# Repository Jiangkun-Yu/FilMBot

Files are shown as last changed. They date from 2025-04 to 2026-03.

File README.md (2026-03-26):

# 📦 FilMBot – A Film-based Electromagnetic Micromanipulator
FilMBot (Film-based ElectroMagnetic driven Robot) is an open-source, low-cost, and DIY-friendly micromanipulator. Designed for high-resolution micromanipulation tasks, FilMBot combines electromagnetic actuation with a soft, film-based kinametic structure to achieve sub-10 μm precision and fast response, all at a total cost of around €100.

This repository provides all necessary hardware files, firmware, and fabrication guidance to replicate and customize FilMBot for use in research, education, or hobby projects.

📄 You can find the original research paper describing FilMBot here: https://doi.org/10.48550/arXiv.2410.23059

## 📁 Project Structure

FilMBot/<br>
│<br>
├── hardware/               &emsp;&emsp;&emsp;&emsp;&emsp;&emsp;&emsp;&emsp;&emsp;&emsp;&emsp;&emsp;&emsp;&emsp;&emsp;&emsp;# Electronics & mechanical design<br>
│   &emsp;&emsp;├── 3D models/           &ensp;&emsp;&emsp;&emsp;&emsp;&emsp;&emsp;&emsp;&emsp;&emsp;&emsp;&emsp;&emsp;# STL files for 3D printed parts<br>
│   &emsp;&emsp;├── cut patterns/        &emsp;&emsp;&emsp;&emsp;&emsp;&emsp;&emsp;&emsp;&emsp;&emsp;&emsp;&emsp;# Laser-cut/printable patterns for film structure<br>
│   &emsp;&emsp;└── schematic and PCB    &ensp;&emsp;&emsp;&emsp;&emsp;&emsp;&emsp;&emsp;&emsp;&emsp;# PCB schematics, board layout, Gerber files ... <br>
│   		&emsp;&emsp;&emsp;&emsp;&emsp;├── 01 Gerber file for ordering PCB/<br>
│   		&emsp;&emsp;&emsp;&emsp;&emsp;├── 02 schematic and bill of electronic components.pdf/<br>
│   		&emsp;&emsp;&emsp;&emsp;&emsp;├── 03 Mega 2560 Rev3_datasheet_from docs.arduino.cc.pdf/<br>
│   		&emsp;&emsp;&emsp;&emsp;&emsp;├── 04 TB6612FNG Hookup Guide.txt/	<br>
│   		&emsp;&emsp;&emsp;&emsp;&emsp;└── 05 TB6612FNG datasheet.pdf/<br>
│<br>
├── firmware/                &emsp;&emsp;&emsp;&emsp;&emsp;&emsp;&emsp;&emsp;&emsp;&emsp;&emsp;&emsp;&emsp;&emsp;&emsp;&emsp;# Arduino firmware<br>
│   &emsp;&emsp;└── FilMBot_Arduino_Code/ <br>
│<br>
├── materials, components and fabrication/     &emsp;&emsp;&emsp;# Cost analysis & fabrication details<br>
│   &emsp;&emsp;└── materials, components and fabrication.docx/<br>
│<br>
└── README.md                &emsp;&emsp;&emsp;&emsp;&emsp;&emsp;&emsp;&emsp;&emsp;&emsp;&emsp;&emsp;&emsp;&emsp;&emsp;# Project overview (this file)<br>

## 🛠️ Hardware Overview
The hardware system includes:

&emsp;&emsp;&emsp;&emsp;&emsp;Microcontroller: Arduino Mega 2560 or compatible ATmega2560 board

&emsp;&emsp;&emsp;&emsp;&emsp;Coil driver: TB6612FNG dual-channel motor drivers

&emsp;&emsp;&emsp;&emsp;&emsp;Power: 12V DC input with step-down converters (to 5V, 3.3V, etc.)

&emsp;&emsp;&emsp;&emsp;&emsp;Interfaces: Joystick + buttons, optional LCD and sensors (current, temperature)

&emsp;&emsp;&emsp;&emsp;&emsp;Structure: Soft film-based body (laser-cut or hand-cut) with permanent magnets

&emsp;&emsp;&emsp;&emsp;&emsp;PCB: Custom-designed for compact and stable operation (or breadboard prototype)

You’ll find:

&emsp;&emsp;&emsp;&emsp;&emsp;📐 3D models in hardware/3D models/

&emsp;&emsp;&emsp;&emsp;&emsp;✂️ Cutting patterns in hardware/cut patterns/

&emsp;&emsp;&emsp;&emsp;&emsp;🔌 Circuit diagrams, PCB, and related instructions and datasheets in hardware/schematic and PCB/

## 💻 Firmware
The firmware supports two control modes:

&emsp;&emsp;&emsp;&emsp;&emsp;Joystick-based telemanipulation (standalone)

&emsp;&emsp;&emsp;&emsp;&emsp;PC command-based control via UART

It runs on a max. 1 kHz (100 Hz by default) interrupt loop for:

&emsp;&emsp;&emsp;&emsp;&emsp;Reading joystick, buttons, and sensors (current, temperature)

&emsp;&emsp;&emsp;&emsp;&emsp;Performing PID control for coil current

&emsp;&emsp;&emsp;&emsp;&emsp;Generating PWM outputs

&emsp;&emsp;&emsp;&emsp;&emsp;Sending data and debug info to LCD or PC

The firmware is modular and easy to extend. To modify or maintain:

&emsp;&emsp;&emsp;&emsp;&emsp;Change pin mappings or parameters in pin_init.h

&emsp;&emsp;&emsp;&emsp;&emsp;Add new features or control logic in FilMBot_Arduino_Code.ino

## 📉 Materials, Components & Fabrication
The total cost of FilMBot is approximately €100. All parts are selected for affordability and global availability.

In materials_and_costs/, you’ll find:

&emsp;&emsp;&emsp;&emsp;&emsp;✔️ A full Bill of Materials with prices

&emsp;&emsp;&emsp;&emsp;&emsp;🔧 A DIY fabrication guide describing each step (cutting, assembly, etc.)

&emsp;&emsp;&emsp;&emsp;&emsp;🛒 A list of suggested vendors and links

FilMBot is designed to be built with only basic tools, with no need for a CNC or cleanroom.

## 🤝 License and Citation
Please cite the original paper when using this work in academic or public projects to help spread the impact of this open-source initiative:

https://doi.org/10.1109/TRO.2026.3658292
and
https://doi.org/10.1109/MARSS65887.2025.11072791 

## 🌟 How to Contribute
We welcome contributions from the community! You can help by:

&emsp;&emsp;&emsp;&emsp;&emsp;Submitting pull requests to improve documentation, firmware, or hardware files

&emsp;&emsp;&emsp;&emsp;&emsp;Sharing your builds and variations

&emsp;&emsp;&emsp;&emsp;&emsp;Reporting issues or suggesting enhancements

Let’s work together to make micromanipulation more accessible and innovative!

## 📬 Contact
Feel free to reach out to the project author:

Jiangkun Yu

Doctoral Researcher

Robotic Instruments Group

Aalto University, Finland

📧 jiangkun.yu@aalto.fi

🌐 www.linkedin.com/in/jiangkun-yu-5265a0278

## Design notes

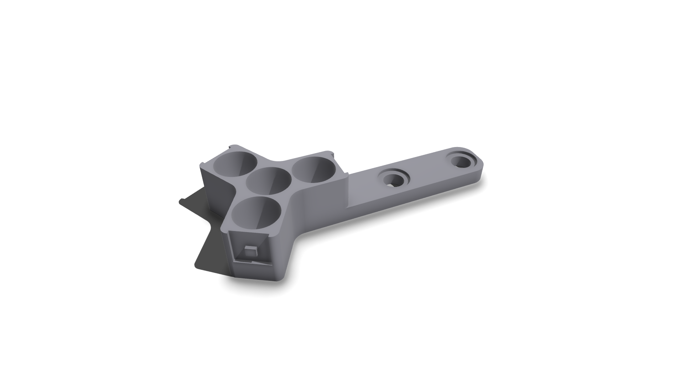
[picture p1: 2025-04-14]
hardware/3D models/Coil holder_3 legged.png

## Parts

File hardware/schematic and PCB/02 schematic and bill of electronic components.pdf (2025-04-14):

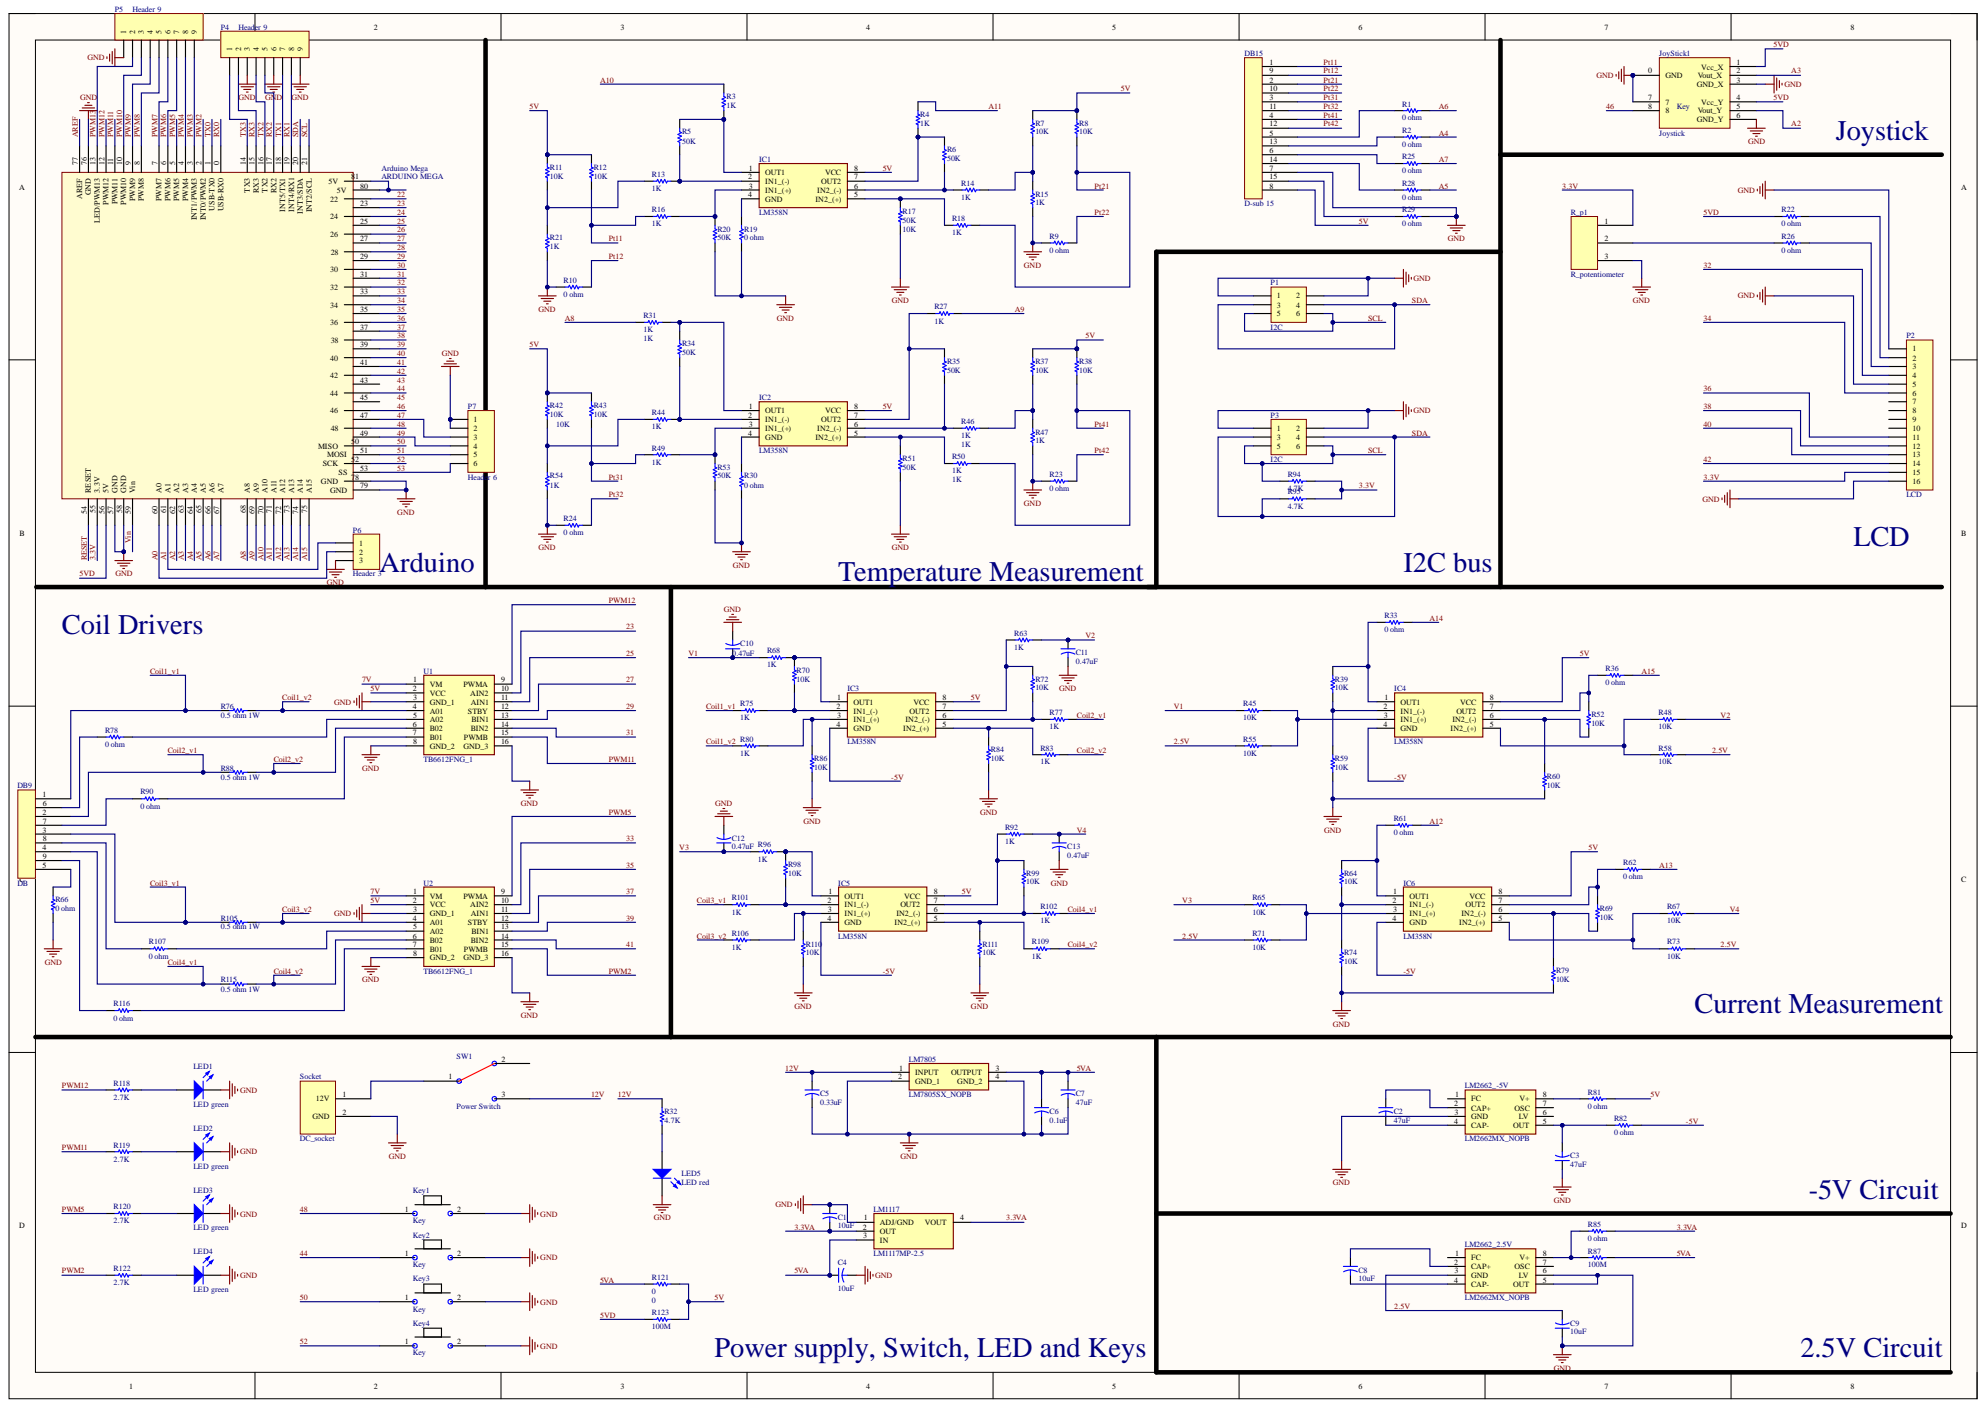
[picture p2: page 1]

6 | | 0 ohm

Coil4_v2 | B01 7 GND_2 8 | 41

47uF | CAP- 4

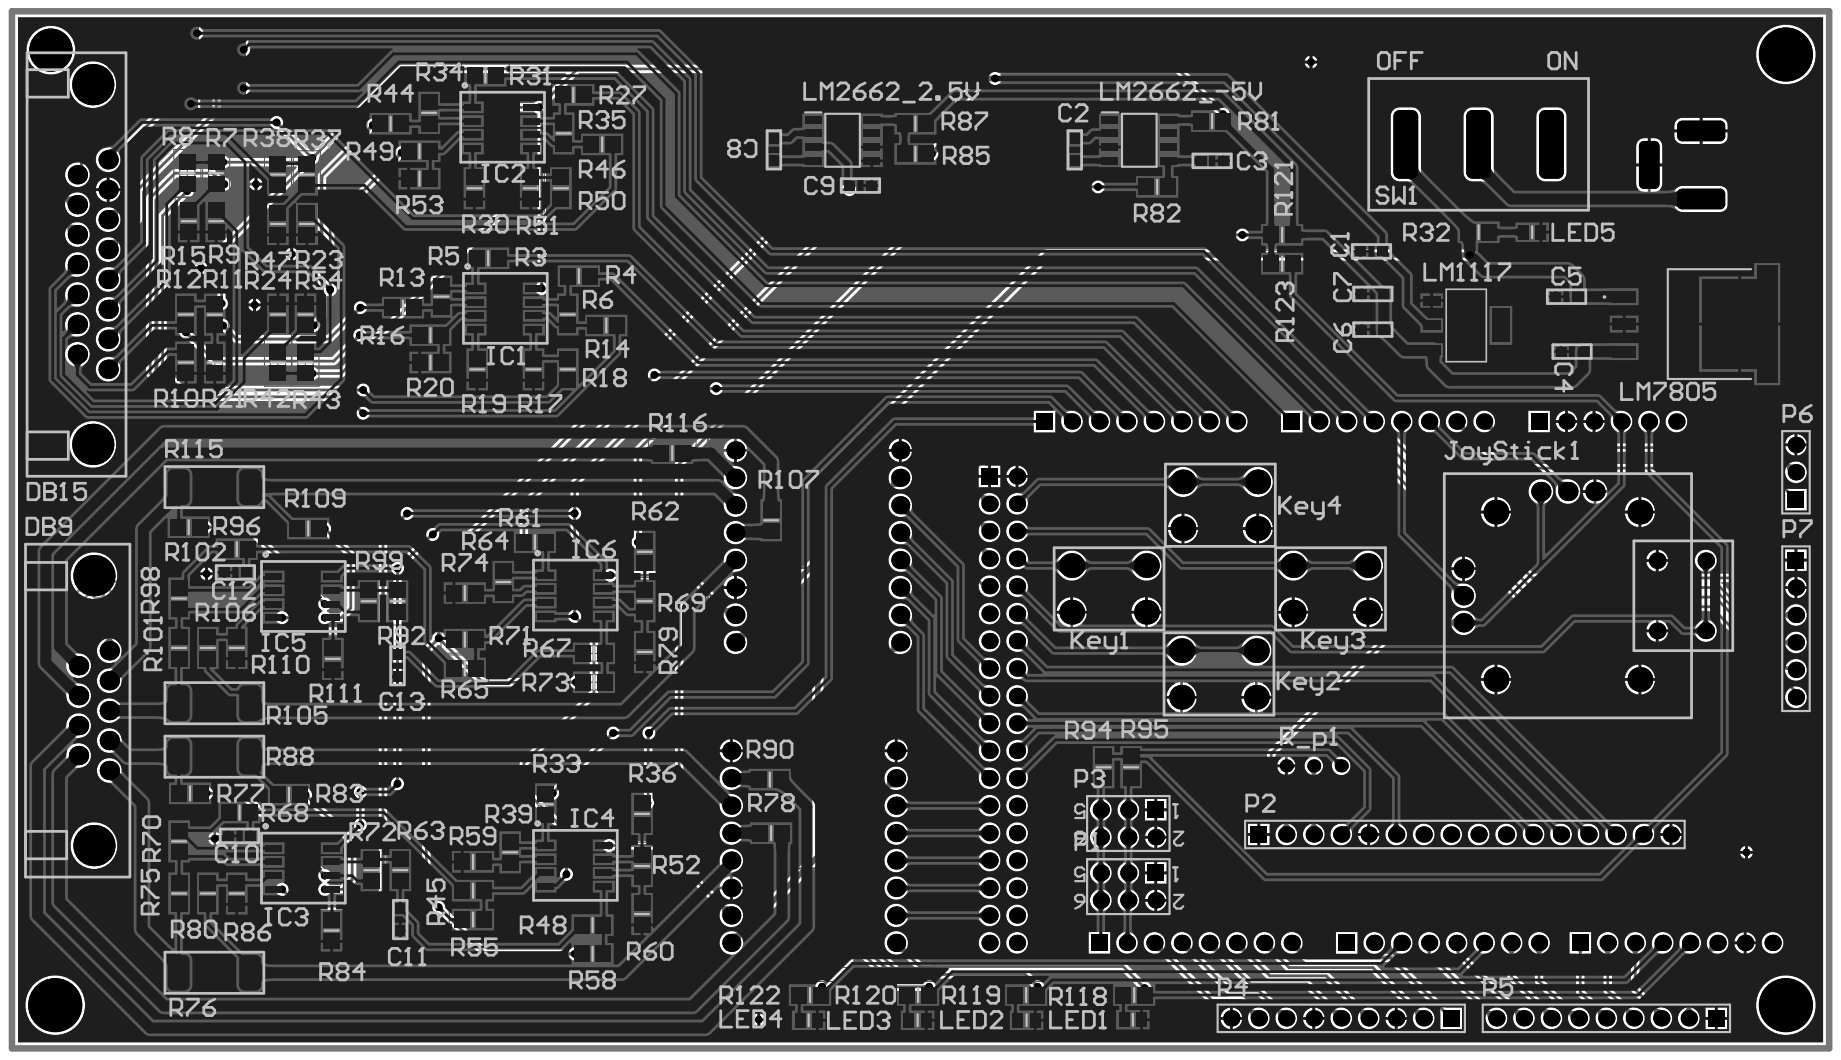
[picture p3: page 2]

Comment | Description | Designator | Footprint | LibRef | Quantity
ARDUINOMEGA | | ArduinoMega | PCBComponent_1 | ARDUINOMEGA | 1
10uF | Capacitor | C1, C4, C8, C9 | C0603 | Cap2 | 4
47uF | Capacitor | C2, C3, C7 | C0603 | Cap2 | 3
0.33uF | Capacitor | C5 | C0603 | Cap2 | 1
0.1uF | Capacitor | C6 | C0603 | Cap2 | 1
0.47uF | Capacitor | C10, C11, C12, C13 | C0603 | Cap2 | 4
DB | | DB9 | PCBComponent_1 | DB | 1
D-sub15 | | DB15 | DB15 | D-sub15 | 1
LM358N | IntegratedCircuit | IC1, IC2, IC3, IC4, IC5, IC6 | 8-SOIC | LM358N | 6
Joystick | | JoyStick1 | PCBComponent_1 | Component_1 | 1
Key | | Key1, Key2, Key3, Key4 | PCBComponent_1 | Key | 4
LEDgreen | Typical REDGaAsLED | LED1, LED2, LED3, LED4 | 6-0805_L | LED1 | 4
LEDred | Typical REDGaAsLED | LED5 | 6-0805_L | LED1 | 1
LM1117MP-2.5 | IntegratedCircuit | LM1117 | SOT230P696X180-4N | LM1117MP-2.5 | 1
LM2662MX_NOPB | IntegratedCircuit | LM2662_2.5V, LM2662_-5V | SOIC127P600X175-8N | LM2662MX_NOPB | 2
LM7805SX_NOPB | IntegratedCircuit | LM7805 | KTT0003B | LM7805SX_NOPB | 1
I2C | Header, 3-Pin, Dual row | P1, P3 | HDR2X3 | Header 3X2 | 2
LCD | Header, 16-Pin | P2 | HDR1X16 | Header 16 | 1
Header 9 | Header, 9-Pin | P4, P5 | HDR1X9 | Header 9 | 2
Header 3 | Header, 3-Pin | P6 | HDR1X3 | Header 3 | 1
Header 6 | Header, 6-Pin | P7 | HDR1X6 | Header 6 | 1
0ohm | Resistor | R1, R2, R9, R10, R19, R22, R23, R24, R25, R26, R28, R29, R30, R33, R36, R61, R62, R66, R78, R81, R82, R85, R90, R107, R116 | 6-0805_M | Res1 | 25
1K | Resistor | R3, R4, R13, R14, R15, R16, R18, R21, R27, R31, R44, R46, R47, R49, R50, R54, R63, R68, R75, R77, R80, R83, R92, R96, R101, R102, R106, R109 | 6-0805_M | Res1 | 28
50K | Resistor | R5, R6, R17, R20, R34, R35, R51, R53 | 6-0805_M | Res1 | 8
10K | Resistor | R7, R8, R11, R12, R37, R38, R39, R42, R43, R45, R48, R52, R55, R58, R59, R60, R64, R65, R67, R69, R70, R71, R72, R73, R74, R79, R84, R86, R98, R99, R110, R111 | 6-0805_M | Res1 | 32
4.7K | Resistor | R32, R94, R95 | 6-0805_M | Res1 | 3
0.5 ohm1W | Resistor | R76, R88, R105, R115 | 2512-L | Res1 | 4
100M | Resistor | R87, R123 | 6-0805_M | Res1 | 2
2.7K | Resistor | R118, R119, R120, R122 | 6-0805_M | Res1 | 4
0 | Resistor | R121 | 6-0805_M | Res1 | 1
R_potentiometer | | R_p1 | PCBComponent_1 | R_potentiometer | 1
DC_socket | | Socket | PCBComponent_1 | DC_socket | 1
Power Switch | | SW1 | PCBComponent_1 | Component_1 | 1
TB6612FNG_1 | Undefinedor Miscellaneous | U1, U2 | ROB14450 | ROB-14450 | 2

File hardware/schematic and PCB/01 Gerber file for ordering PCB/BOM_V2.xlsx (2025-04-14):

Comment | Designator | Footprint | LCSC Part #
10uF | C1, C4, C8, C9 | C0603 | C19702
47uF | C2, C3, C7 | C0603 | C140782
0.33uF | C5 | C0603 | C1615
0.1uF | C6 | C0603 | C14663
0.47uF | C10, C11, C12, C13 | C0603 | C1623
LM358N | IC1, IC2, IC3, IC4, IC5, IC6 | 8-SOIC | C504545
LED green | LED1, LED2, LED3, LED4 | 6-0805_L | C2297
LED red | LED5 | 6-0805_L | C2286
LM1117MPX-3.3 | LM1117 | SOT230P696X180-4N | C9662
LM2662MX_NOPB | LM2662_2.5V, LM2662_-5V | SOIC127P600X175-8N | C134022
LM7805SX_NOPB | LM7805 | KTT0003B | C507146
1K | R3, R4, R13, R14, R15, R16, R18, R21, R27, R31, R44, R46, R47, R49, R50, R54, R63, R68, R75, R77, R80, R83, R92, R96, R101, R102, R106, R109 | 6-0805_M | C17513
50K | R5, R6, R17, R20, R34, R35, R51, R53 | 6-0805_M | C316211
10K | R7, R8, R11, R12, R37, R38, R39, R42, R43, R45, R48, R52, R55, R58, R59, R60, R64, R65, R67, R69, R70, R71, R72, R73, R74, R79, R84, R86, R98, R99, R110, R111 | 6-0805_M | C17414
4.7K | R32, R94, R95 | 6-0805_M | C17673
0.3 ohm 1W | R76, R88, R105, R115 | 2512-L | C474208
2.7K | R118, R119, R120, R122 | 6-0805_M | C17530

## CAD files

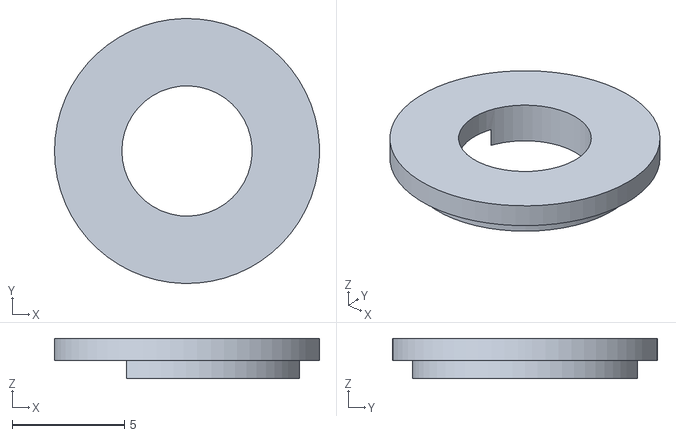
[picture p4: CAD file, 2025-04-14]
hardware/3D models/Coil shoulder_6.0mm.STL
11.8 x 11.8 x 1.80

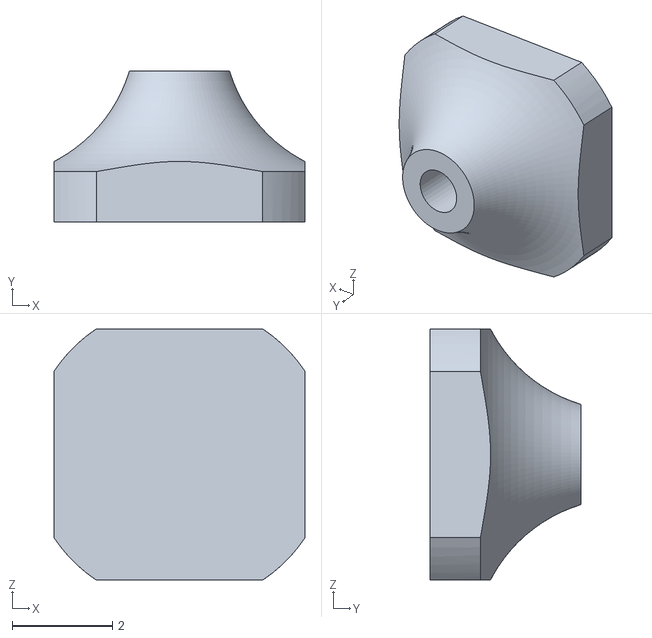
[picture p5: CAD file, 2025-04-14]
hardware/3D models/needle holder V3.STL
5.00 x 3.00 x 5.00

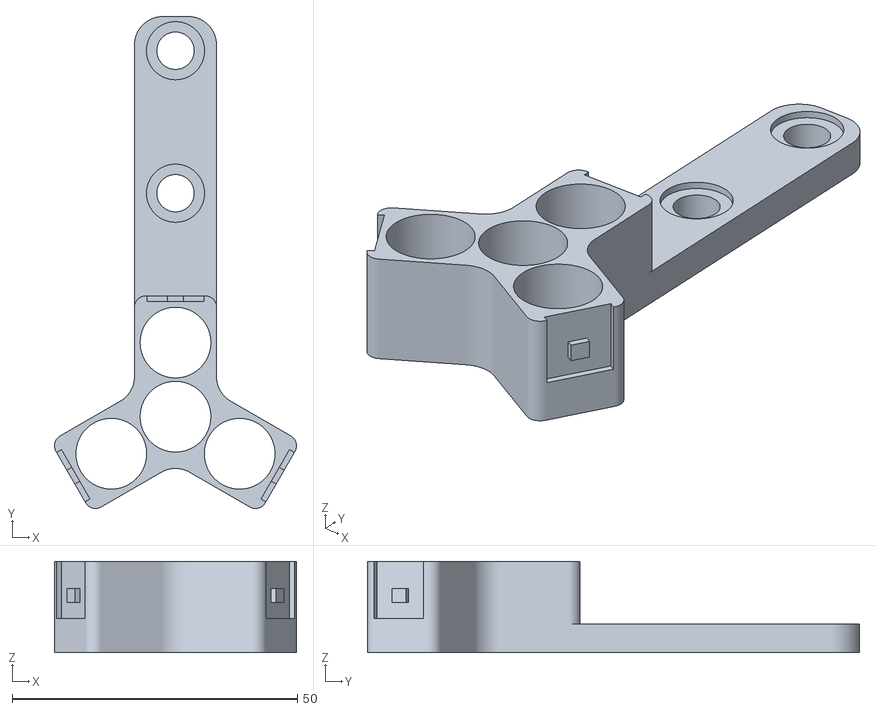
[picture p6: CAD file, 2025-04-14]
hardware/3D models/Coil holder_3 legged.stl
42.5 x 86.3 x 16.0

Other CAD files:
hardware/3D models/PCB Box_Part2_V4.STL
hardware/3D models/PCB Box_Part1_V4.STL

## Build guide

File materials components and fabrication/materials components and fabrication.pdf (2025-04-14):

FILMBOT HARDWARE COST ANALYSIS
Components | Fabrication | Price
Solenoid coils (copper wire) | Hand-wound. | 7.2 € [1]
Solenoid coil core (S355J2 steel rod) | Cutting with a saw, smoothing with a file. | 0.4 € [2]
NdFeB magnets | Direct purchasing. | 1.2 € [3]
Film (plastic or paper) | Laser-cut or print and hand-cut. | 0.2 € [4]
Needle | Heating and hot drawing, or 3D printing. | 0.2 € [5]
3D-printed components | 3D printing. | 1 € [6]
Double-side tape | Hand-cut. | 0.1 €
PCB with assembly | Direct purchasing. | 13.5 € [7]
Joystick | Soldering. | 4.2 € [8]
Microcontroller Mega 2560 | Direct purchasing. | 22.4 € [9]
Coil driver | Direct purchasing. | 20 € [10]
12V power supply | Direct purchasing. | 13.6 € [11]
Cables and connectors | Soldering. | 11 € [12]
PT1000 | Soldering. | 7.6 € [13]
Total | | 102.6 €
Please refers paper “FilMBot: A High-Speed Soft Parallel Robotic Micromanipulator” (https://doi.org/10.48550/arXiv.2410.23059) and “FilMBot: Towards 100-euro DIY-friendly high-speed robotic micromanipulator”
for detailed materials, components and fabrications.

Reference:
[1] “RS PRO 0.25mm Enamelled Copper Wire, 30 AWG 1100m Reel | RS PRO,” RS Finland. Accessed: Apr. 10, 2025.
[Online]. Available: https://fi.rsdelivers.com/product/rs-pro/rs-pro-025mm-enamelled-copper-wire-30-awg-1100m/0357716
[2] “Warma vedetty pyörötanko 6mm 1,5m.” Accessed: Apr. 10, 2025. [Online]. Available: https://www.puuilo.fi/warmavedetty-pyorotanko-6mm-1-5m
[3] W. AG, “Disc magnet self-adhesive 10 x 0,6 mm, Nickel-plated,” Supermagnete. Accessed: Apr. 10, 2025. [Online]. Available: https://www.supermagnete.fi/adhesive-magnets-neodymium/disc-magnet-self-adhesive-10mm-0.6mm_S-10-0.6-STIC
[4] “muovitasku A4/120mic 2-sivua auki värilajitelma Polypropeeni 100kpl.” Accessed: Apr. 10, 2025. [Online]. Available: https://kauppa.rckfinland.fi/130281-muovitasku-a4-120mic-2-sivua-auki-varilajitelma-polypropeeni-100kpl.html
[5] “200PCS Glass Capillary Tube Micro Hematocrit Tubing Melting Tube,” Fruugo. Accessed: Apr. 10, 2025. [Online]. Available: https://www.fruugo.fi/200pcs-glass-capillary-tube-micro-hematocrit-tubing-melting-tube-multi-purposeglass-tube-for-clinic-hospital-use-red/p-136337047-287521506?language=en
[6] “PLA 3D-filamentti Universal, 1,75 mm, 1 kg | Clas Ohlson.” Accessed: Apr. 10, 2025. [Online]. Available:
https://www.clasohlson.com/fi/PLA-3D-filamentti-Universal,-1,75-mm,-1-kg/p/38-7986-1
[7] “PCB Prototype & PCB Fabrication Manufacturer - JLCPCB.” Accessed: Apr. 10, 2025. [Online]. Available: https://jlcpcb.com/
[8] “COM-09032,” DigiKey Electronics. Accessed: Apr. 10, 2025. [Online]. Available: https://www.digikey.fi/en/products/detail/sparkfun-electronics/COM-09032/6823623
[9] “Arduino Mega 2560 R3 -yhteensopiva kehityskortti Mega2560 Ch340 | Fyndiq.” Accessed: Apr. 10, 2025. [Online].
Available: https://fyndiq.fi/tuote/arduino-mega-2560-r3-yhteensopiva-kehityskortti-mega2560-ch340-5266901d7fc74811/
[10] “2pcs TB6612FNG Dual DC Stepper Motor Driver Module, Dual Driver Controller Board H Bridge for DC Step TB6612FNG Module : Amazon.de: Business, Industry & Science.” Accessed: Apr. 10, 2025. [Online]. Available: https://www.amazon.de/TB6612FNG-Stepper-Driver-Module-Controller/dp/B09MN8F1SD/
[11] reichelt elektronik G. I. T. webmaster@reichelt.de, “V-TAC Desktop power supply, 60 W, 12 V, 5 A | Fixed-voltage
power supply units at very favourable prices | reichelt elektronik.” Accessed: Apr. 10, 2025. [Online]. Available:
https://www.reichelt.com/fi/en/shop/product/desktop_power_supply_60_w_12_v_5_a-215628
[12] “Connectors, Interconnects | D-Sub, D-Shaped Connectors | D-Sub Connector Assemblies,” DigiKey Electronics.
Accessed: Apr. 10, 2025. [Online]. Available: https://www.digikey.fi/en/products/filter/d-sub-d-shaped-connectors/d-sub-connector-assemblies/439
[13] reichelt elektronik G. I. T. webmaster@reichelt.de, “YAGEO NEXENSOS Platinum temperature sensor, Cl. B, 1000
ohms | Temperature and moisture sensors at very favourable prices | reichelt elektronik.” Accessed: Apr. 10, 2025.
[Online]. Available: https://www.reichelt.com/fi/en/shop/product/platinum_temperature_sensor_cl_b_1000_ohms-151238

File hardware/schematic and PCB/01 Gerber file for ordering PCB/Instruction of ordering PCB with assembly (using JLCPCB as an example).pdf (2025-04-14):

## Instructions for ordering PCB with assembly

Here, using JLCPCB as an example, ordering from other manufacturers will be similar.

1. Get your files ready, generally at least need all Gerber files. If you also need assembly, get BOM and CPL file ready.
2. Go to jlcpcb.com:

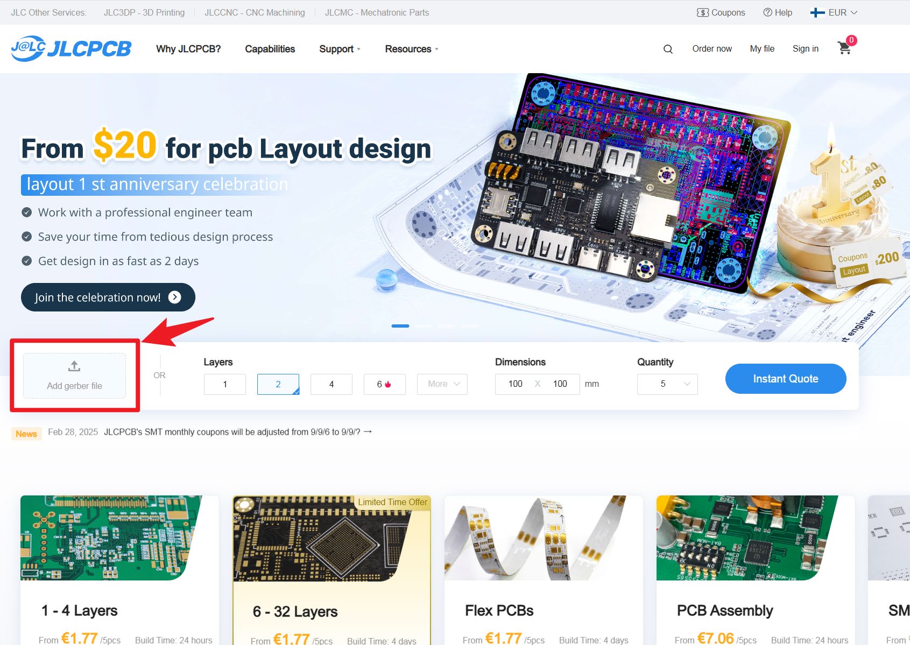
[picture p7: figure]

3. Drag the “Gerber files.rar” to the box, and wait until it shows the PCB:

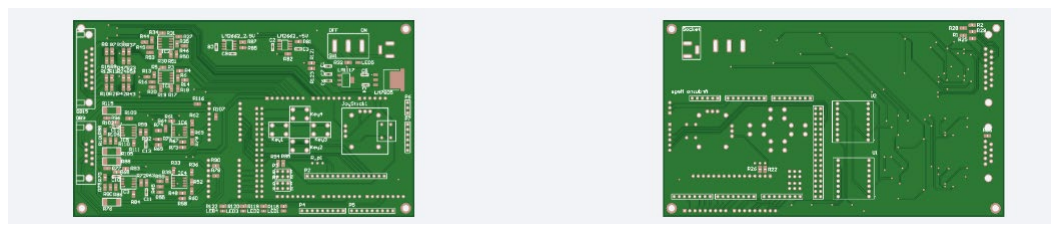
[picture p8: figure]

4. Activate the “PCB Assembly” option, and select Qty as you need:

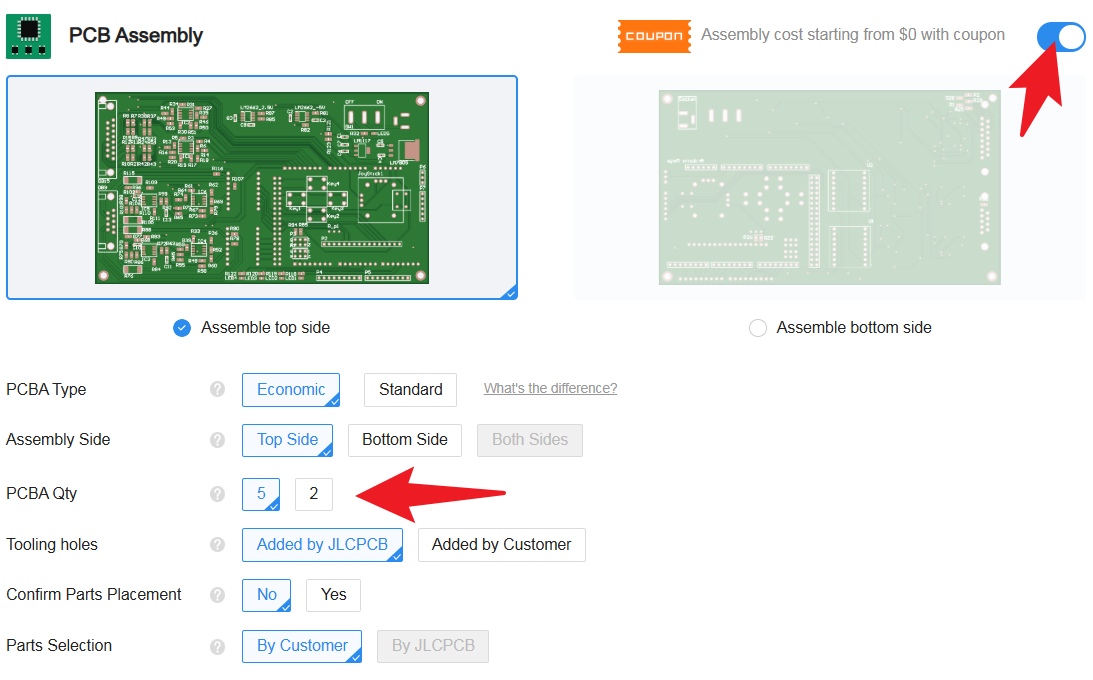
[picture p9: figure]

5. Other options can be modified as needed. Otherwise, the default can be used. Then click Next. Select Top side for assembly.

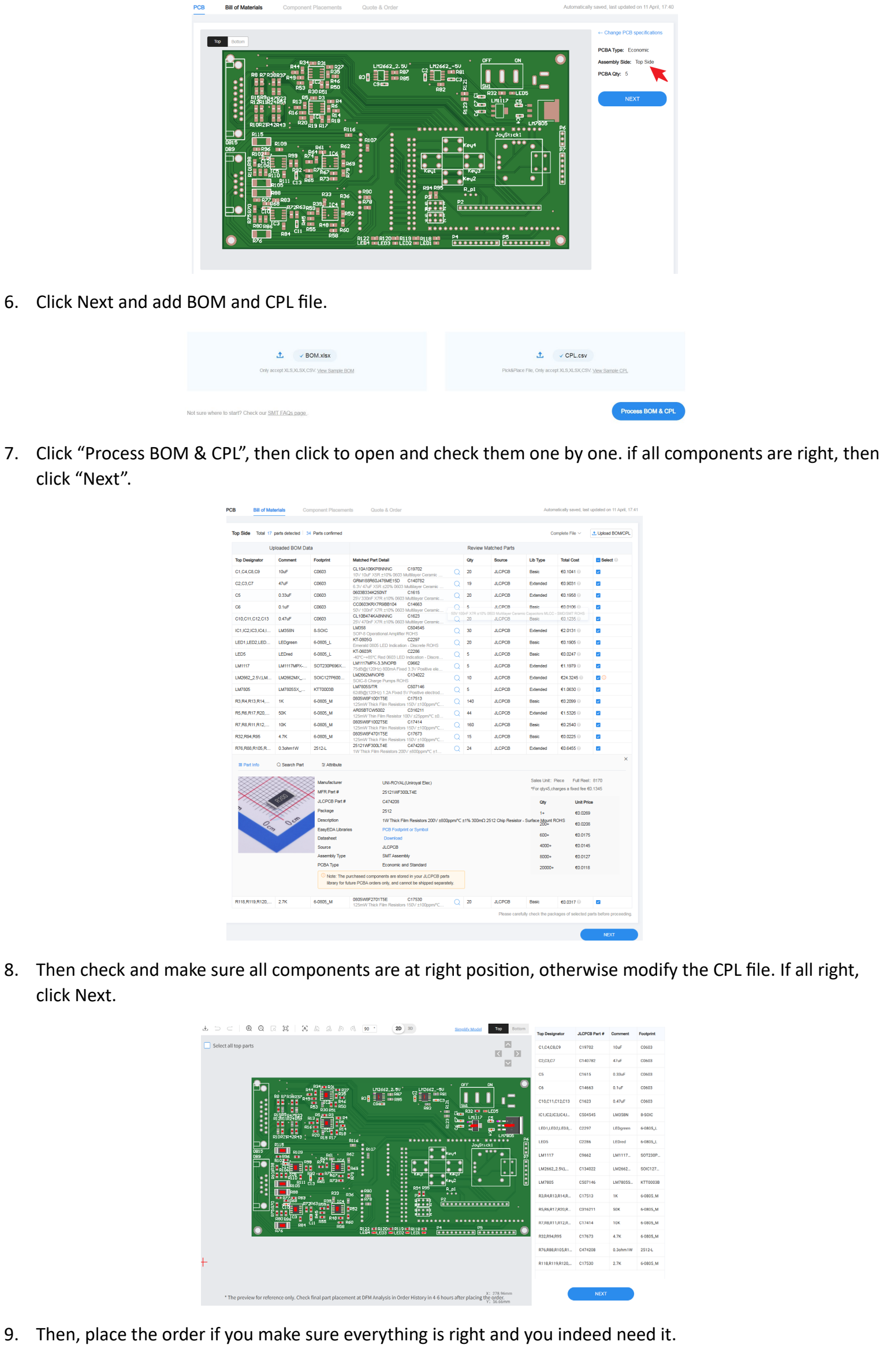
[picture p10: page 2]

6. Click Next and add BOM and CPL file.
7. Click “Process BOM & CPL”, then click to open and check them one by one. if all components are right, then click “Next”.
8. Then check and make sure all components are at right position, otherwise modify the CPL file. If all right, click Next.
9. Then, place the order if you make sure everything is right and you indeed need it.

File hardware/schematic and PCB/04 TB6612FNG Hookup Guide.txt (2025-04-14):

Please find it in learn.sparkfun.com:

https://learn.sparkfun.com/tutorials/tb6612fng-hookup-guide/all

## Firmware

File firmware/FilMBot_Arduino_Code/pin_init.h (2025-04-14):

#ifndef PIN_INIT_H
#define PIN_INIT_H

#include <Arduino.h>

////**********************************Pin definition*******************************//
#define Key1_Pin 48     //Key3
#define Key2_Pin 44     //Key4
#define Key3_Pin 50     //Key5
#define Key4_Pin 52     //Key6
#define JoyX_Pin A2    //Joystick X axis
#define JoyY_Pin A3    //Joystick Y axis
#define JoyK_Pin 46     //Joystick Key


#define Tem_Pin_1 A11       //Temperature of coil 1
#define Tem_Pin_2 A8        //Temperature of coil 1
#define Tem_Pin_3 A9        //Temperature of coil 1
#define Tem_Pin_4 A10       //Temperature of coil 1
#define I_Pin_1 A13         //Current of coil 4
#define I_Pin_2 A15         //Current of coil 2
#define I_Pin_3 A14         //Current of coil 2
#define I_Pin_4 A12         //Current of coil 4
#define H_Pin_1 A6         //Hall sensor of coil 2
#define H_Pin_2 A5         //Hall sensor of coil 2
#define H_Pin_3 A7         //Hall sensor of coil 2
#define H_Pin_4 A4         //Hall sensor of coil 4



#define AIN1 25
#define AIN2 23
#define BIN1 29
#define BIN2 31
#define PWMA 12
#define PWMB 11
#define STBY1 27

#define AIN3 35
#define AIN4 33
#define BIN3 39
#define BIN4 41
#define PWMC 5
#define PWMD 2
#define STBY2 37

#define test_pin 51
#define cam_pin 47
////**********************************Pin definition***************************************//


#endif

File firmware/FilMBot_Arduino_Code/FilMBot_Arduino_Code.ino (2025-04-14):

//////*******************FilMBot Arduino Code*****************//////
// 
// 2025.04.13
// 
// Hardware:
//    Arduino Mega 2560, with 16 MHz main clock
// 
// Liabray:
//    At least the following libraries should be included before runing:
//      1. SparkFun_TB6612, included in FilMBot.ino (main)
//      2. PID, by Brett Beauregard, included in current loop.cpp
//
// Control Mode:
//         Use control_flag to set the control mode, either use the Key or the UART command to set it.
//             control_flag == 0, means using UART_PWM_control_mode, UART giving PWM reference
//             control_flag == 1, means using UART_PID_control_mode, current loop is closed and UART giving current reference
//             control_flag == 2, means using Joystick_control_mode, Joystick to give PWM reference
//             control_flag == 3..., means specific funtion, you can define it as you want, e.g., here using control_flag == 3 to shutdown the PWM output as 0
// 
//         In UART_control_mode:
//           by sending "Acoil1_ref,coil2_ref,coil3_ref,coil4_ref,control_flag,B" and 'A' and 'B' are head and tail, coil#_ref is positive integer, as reference values for coil# (command must follow the format, No Line Ending)
//           1. In UART_PWM_control_mode, value (coil#_ref - 1299)        will be duty cycle and apply to coil#
//           2. In UART_PID_control_mode, value (coil#_ref - 1299)/1500   will be current reference and apply to coil#
// 
//         In Joystick_control_mode:
//             by using Key2 to switch between these two mode (in the case control_flag == 2)
//             1. Joystick_absolute_control_mode, use Joystick to give absolute value for the coil PWM, joystic_x and joystick_y is correspongding coil 1 and 3, by pressing the key intergrated in the joystick, switching to coil 2 and 4
//             2. Joystick_reletive_control_mode, use Joystick to give adding value to each axis, joystic_x giving increment to coil1, and joystick_y giving increment to coil2 and 3
// 
// The way to use the code:
//        1. by default, it is in Joystick_absolute_control_mode;
//        2. Press Key2 to go to  Joystick_reletive_control_mode, and press again to go back;
//        3. Press Key1 to go to  UART_control_mode, and the Joystick is not valid anymore.
//        4. No matter in which mode, UART command is always valid, as it always set the control_flag in each UART command. 
// 
// 
//////********************************************************//////


#include <SparkFun_TB6612.h>
#include "serial.h"
#include "pin_init.h"
#include "key_joy_read.h"
#include "lcd.h"
#include "sensor_read.h"
#include "current_loop.h"
#include "lcd.h"


////***************************************Motor driver SparkFun_TB6612 ************************************//
// these constants are used to allow you to make your motor configuration 
// line up with function names like forward.  Value can be 1 or -1
const int offsetA = 1;
const int offsetB = 1;
const int offsetC = 1;
const int offsetD = 1;

// Initializing motors.   change the orders to fit with the coils position
Motor motor3 = Motor(AIN1, AIN2, PWMA, offsetA, STBY1);
Motor motor2 = Motor(BIN1, BIN2, PWMB, offsetB, STBY1);
Motor motor4 = Motor(AIN3, AIN4, PWMC, offsetC, STBY2);
Motor motor1 = Motor(BIN3, BIN4, PWMD, offsetD, STBY2);
////***************************************Motor driver SparkFun_TB6612 ************************************//

////***************************************Varible Initialization************************************//
int A_fre = 100;  //frequency of the main loop, in Hz
int control_flag = 2;           // Not here, by dafult, control_flag is 2, means using Joystick to give PWM reference  
bool ser_flag = false;          // reset as false at begaining, but will preset as 1 when serial external event happend
bool timer_flag = false;        // reset as false at begaining, but will preset as 1 every timer interrupt
bool serial_print_flag= false;  // reset as false to deactive the UART data print, which uses a lot of time to print
bool lcd_flag = true;           // reset as false to deactive the LCD, which uses a lot of time to dispaly

int PWM_Coil[4] = {0};
int PID_PWM_out[4] = {0};
int coil=0, mode=1; 
int ErrorFlag = 0, FunFlag1 = 0, FunFlag2 = 0, FunFlag3 = 0, FunFlag4 = 0;
int PIDFlag = 0, PID_start_Flag = 0; 
double Ref_list[6] = {0, -0.1, 0.2, -0.4, 0.25, -0.45};
double Ref_I_old[4] = {0};

int count_i = 0;
int uart_i = 0;

int PWM_tran_flag = 0;
int PID_slow_i_flag[4] = {1,1,1,1};
int PID_slow_i[4] = {0,0,0,0};
int PID_ref_i[4] = {0,0,0,0};
////***************************************Varible Initialization************************************//


void setup() {
  //Set timer 1 and 3, fast PWM mode, ICRn as TOP count, the max duty cycle value for PWM is 1599
  pinMode(11, OUTPUT);
  pinMode(12, OUTPUT);
  TCCR1A = _BV(COM1A1) | _BV(COM1B1) | _BV(WGM11);
  TCCR1B = _BV(WGM13) | _BV(WGM12) | _BV(CS10);
  ICR1 = 1600;
  
  pinMode(2, OUTPUT);
  pinMode(5, OUTPUT);
  TCCR3A = _BV(COM3A1) | _BV(COM3B1) | _BV(WGM31);
  TCCR3B = _BV(WGM33) | _BV(WGM32) | _BV(CS30);
  ICR3 = 1600;                  // the max duty cycle value for PWM is 1599 

  //Initialize JoyStick and Key
  joy_key_init();

  //Initialize PID
  current_loop_init();

  //Initialize LCD
  if (lcd_flag){ lcd_initial(); }

  //Initialize Uart
  Serial.begin(500000);     //Set Uart serial port, baudrate 500000

  //Initialize current and temperature sensing, mainly for getting initial shift
  sensor_init();
  delay(500);

  //Set Interrupt 4
  noInterrupts();           // disable all interrupts
  TCCR4A = 0;
  TCCR4B = 0;
  TCNT4  = 0;
  OCR4A = 2000000 / A_fre;  // by seting A_fre t set the frequency of the Interrupt 4, which will work as the main function enabling interuput
  TCCR4B |= (1 << WGM42);   // CTC mode
  TCCR4B |= (1 << CS41);    // 8 prescaler 
  TIMSK4 |= (1 << OCIE4A);  // enable timer compare interrupt
  interrupts();             // enable all interrupts
}


void loop() {
  // main code, running repeatedly accoring timer_flag preset by Interrupt 4:

  if(timer_flag)          // the main function will wait here unless the timer_flag got preset in the interupt function
  {
    count_i ++;
    if(count_i > 30000){ count_i = 300; }
    if(count_i == 200) { PID_start_Flag = 1; }

    // read the state of joystick and key
    joy_key_read();
  
    //use key of the joystick to selest which coil to contro in Joystick_absolute_control_mode
    if(JoyK_value == 0){
      while(JoyK_value == 0) JoyK_value = digitalRead(JoyK_Pin);  // "while" is used for remove the hand tremor when pressing the key
      coil = 1 - coil;  // when the flag "coil" is 0, coil 1 and coil 3 is controled in Joystick_absolute_control_mode, otherwise, coil 2 and 4 is controlled
    }
  
    // set PWM output value when mode is 0, Joystick_absolute_control_mode
    if( (FunFlag2 == 0)&& (PIDFlag == 0)){
      PWM_Coil[0] = JoyX_value * (1-coil);
      PWM_Coil[1] = JoyX_value * coil;
      PWM_Coil[2] = JoyY_value * (1-coil);
      PWM_Coil[3] = JoyY_value * coil;
    }
  
    //use Key1 to deactive or activate the current loop and Joystick control mode
    if(Key1_value == 0){
      while(Key1_value == 0) Key1_value = digitalRead(Key1_Pin);
      PIDFlag = 1 - PIDFlag;
      control_flag = 0;
    }

    //use Key2 to deactive or activate Joystick_reletive_control_mode
    if(Key2_value == 0){
      while(Key2_value == 0) Key2_value = digitalRead(Key2_Pin);
      FunFlag2 = 1 - FunFlag2;
      control_flag = 2;   // control_flag == 2 means using Joystick to give reference
    }
    
    if(Key3_value == 0){
      while(Key3_value == 0) Key3_value = digitalRead(Key3_Pin);
      FunFlag3 = 1 - FunFlag3;
    }
  
    if(Key4_value == 0){
      while(Key4_value == 0) Key4_value = digitalRead(Key4_Pin);
      FunFlag4 = 1 - FunFlag4;
    }
    
    // some functions
    if(FunFlag2 == 1){  // Joystick_reletive_control_mode
       PWM_Coil[0] = PWM_Coil[0] + JoyX_value*0.006;
       PWM_Coil[1] = PWM_Coil[1] + JoyY_value*0.003;
       PWM_Coil[2] = PWM_Coil[2] - JoyY_value*0.003;
       PWM_Coil[3] = 0;
    }
    if(FunFlag3 == 1){  // set all PWM duty cycle as 200, for testing
      PWM_Coil[0] = 200;
      PWM_Coil[1] = 200;
      PWM_Coil[2] = 200;
      PWM_Coil[3] = 200;
    }
    if(FunFlag4 == 1){  // reset as 0
      PWM_Coil[0] = 0;
      PWM_Coil[1] = 0;
      PWM_Coil[2] = 0;
      PWM_Coil[3] = 0;
    }
  
    //start pid loop for current control
    if (PID_start_Flag == 1){
      current_pid_setRef(0, 0, 0, 0);
      current_pid_start();
      PIDFlag = 1;
      PID_start_Flag = 0;
    }

    //Read commonds from external device via UART, in a formate "A,coil1_ref,coil2_ref,coil3_ref,coil4_ref,control_flag,B"
    //where 'A' and 'B' are head and tail for checking
    //coil#_ref are reference values for coil#, if in current loop actived mode, then use it as current loop reference;
    //if in PWM control mode, use it as PWM duty cycle value
    // Note the scale converting, detailed in serial.cpp
    if(ser_flag){
      for(int i = 0; i < 4; i++) { Ref_I_old[i] = Ref_I[i]; }
      uart_receive();
      for(int i = 0; i < 4; i++) { Ref_I[i] = Ref_Coil[i];  }
      if ( (abs(Ref_I_old[0] - Ref_I[0]) > 0.05)||(abs(Ref_I_old[1] - Ref_I[1]) > 0.05)||(abs(Ref_I_old[2] - Ref_I[2]) > 0.05)||(abs(Ref_I_old[3] - Ref_I[3]) > 0.05) ){
        PWM_tran_flag = 1;
      }
      
      for (int i = 0; i < 4; i++) { 
        if(Ref_I_old[i] != Ref_I[i]){
          PID_ref_i[i] = 400; // in this time, the fine adjustment for PID will not be used
        }
      }
      
      ser_flag = false;
    }
    if (control_flag == 1){ PIDFlag = 1; }  // control_flag == 1 means using PID control mode, uart giving current
    else {  PIDFlag = 0; }                  

    //read current value (as well as temperature) before the current loop
    sensor_read();

    // run pid computation
    if(PIDFlag==1){
      
      //if Ref_I changed suddenly over 0.05 A, run PWM-I translate function, to have less response time, coeefecients are from regression
      if(PWM_tran_flag != 0){
        if(PWM_tran_flag == 1){
          if ( abs(Ref_I_old[0] - Ref_I[0]) > 0.05 ){
            PID_PWM_out[0] = PID_PWM_out[0] + 1900 * (Ref_I[0] - Ref_I_old[0]) * 1;
          }
          if ( abs(Ref_I_old[1] - Ref_I[1]) > 0.05 ){
            PID_PWM_out[1] = PID_PWM_out[1] + 1900 * (Ref_I[1] - Ref_I_old[1]) * 1;
          }
          if ( abs(Ref_I_old[2] - Ref_I[2]) > 0.05 ){
            PID_PWM_out[2] = PID_PWM_out[2] + 2000 * (Ref_I[2] - Ref_I_old[2]) * 1;
          }
          if ( abs(Ref_I_old[3] - Ref_I[3]) > 0.05 ){
            PID_PWM_out[3] = PID_PWM_out[3] + 1900 * (Ref_I[3] - Ref_I_old[3]) * 1;
          }
        }
        PWM_tran_flag ++;
        if (PWM_tran_flag > 8){
          PWM_tran_flag = 0;
        }        
      } 
      else{
        current_pid_setRef(Ref_I[0], Ref_I[1], Ref_I[2], Ref_I[3]); 
        current_pid_compute();
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

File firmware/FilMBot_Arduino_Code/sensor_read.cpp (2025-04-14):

#include "sensor_read.h"
#include "pin_init.h"

int Tem_AD_1 = 0,Tem_AD_2 = 0,Tem_AD_3 = 0,Tem_AD_4 = 0;
double Tem_value_1 = 0,Tem_value_2 = 0,Tem_value_3 = 0,Tem_value_4 = 0;
double Tem_offset_1 = 0,Tem_offset_2 = 0,Tem_offset_3 = 0,Tem_offset_4 = 0;

//Current related varibles
int I_AD_1 = 0, I_AD_2 = 0, I_AD_3 = 0, I_AD_4 = 0;
double I_value_1 = 0, I_offset_1 = 0.0, I_amp_1 = 1;
double I_value_11 = 0;
double I_value_2 = 0, I_offset_2 = 0.0, I_amp_2 = 1;
double I_value_3 = 0, I_offset_3 = 0.0, I_amp_3 = 1;
double I_value_4 = 0, I_offset_4 = 0.0, I_amp_4 = 1;

int FilBuf_I1[8]  ={0}, FilBuf_I2[8]  ={0}, FilBuf_I3[8]  ={0}, FilBuf_I4[8]  ={0};
double Fil_I1 = 0, Fil_I2 = 0, Fil_I3 = 0, Fil_I4 = 0;


void sensor_init(){
  OCR1A = 0;
  OCR2A = 0;
  OCR3A = 0;
  OCR4A = 0;
  delay(300);
  
  for(int i = 0; i < 10; i++){
    delay(20);
    I_AD_1 = analogRead(I_Pin_1);
    I_AD_2 = analogRead(I_Pin_2);
    I_AD_3 = analogRead(I_Pin_3);
    I_AD_4 = analogRead(I_Pin_4);

    I_offset_1 += ( -I_AD_1 * 0.001691358901341 + 0.910755504848910 )* I_amp_1;
    I_offset_2 += ( -I_AD_2 * 0.001701865599424 + 0.912337950070264 )* I_amp_2;
    I_offset_3 += ( I_AD_3 * 0.001694428848601 - 0.910198662019227 )* I_amp_3;
    I_offset_4 += ( I_AD_4 * 0.001688722587740 - 0.911320472952832 )* I_amp_4;

  }
  
  I_offset_1 = I_offset_1 / 10;
  I_offset_2 = I_offset_2 / 10;
  I_offset_3 = I_offset_3 / 10;
  I_offset_4 = I_offset_4 / 10;

}

void sensor_read(){
   //Temperature
   Tem_AD_1 = analogRead(Tem_Pin_1);
   Tem_AD_2 = analogRead(Tem_Pin_2);
   Tem_AD_3 = analogRead(Tem_Pin_3);
   Tem_AD_4 = analogRead(Tem_Pin_4);
   
   //the coeffecient are from current calibrition
   Tem_value_1 = -1.1863 + 0.11366 * Tem_AD_1;
   Tem_value_2 = -1.1863 + 0.11366 * Tem_AD_2;
   Tem_value_3 = -1.1863 + 0.11366 * Tem_AD_3;
   Tem_value_4 = -1.1863 + 0.11366 * Tem_AD_4;

  //Current
  I_AD_1 = analogRead(I_Pin_1);
  I_AD_2 = analogRead(I_Pin_2);
  I_AD_3 = analogRead(I_Pin_3);
  I_AD_4 = analogRead(I_Pin_4);

  // the coeffecient are from current calibrition
  I_value_1 = ( -I1_Ave(I_AD_1) * 0.001691358901341 + 0.910755504848910 )* I_amp_1 - I_offset_1;
  I_value_2 = ( -I2_Ave(I_AD_2) * 0.001701865599424 + 0.912337950070264 )* I_amp_2 - I_offset_2;
  I_value_3 = ( I3_Ave(I_AD_3) * 0.001694428848601 - 0.910198662019227 )* I_amp_3 - I_offset_3;
  I_value_4 = ( I4_Ave(I_AD_4) * 0.001688722587740 - 0.911320472952832 )* I_amp_4 - I_offset_4;
  
}
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
